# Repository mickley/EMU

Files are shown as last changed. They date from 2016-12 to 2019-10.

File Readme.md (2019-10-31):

# Environmental Microcontroller Units (EMUs)

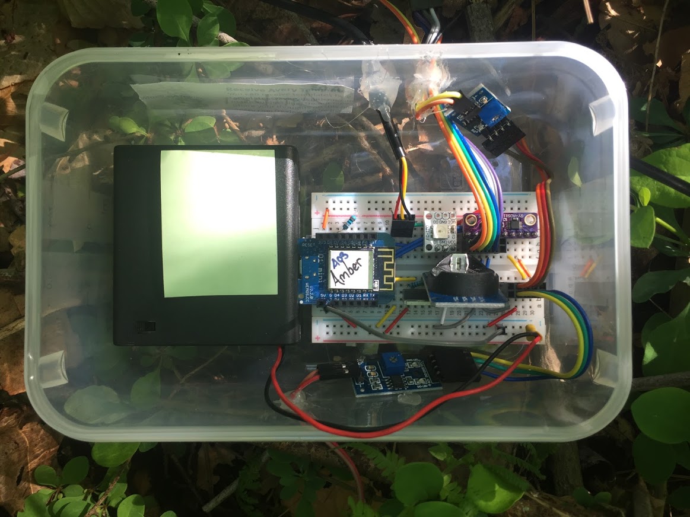
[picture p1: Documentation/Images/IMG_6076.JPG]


This repository stores code, documentation, and analyses for Environmental Microcontroller Units (EMUs). We detail their use in our paper for measuring aspects of microenvironment: temperature, humidity, light, and soil moisture all for less than $20 in hardware costs. However, their flexible nature means that they can be used in a variety of research situations where inexpensive sensors are required.

If this work is useful in your research, please cite our paper:

**Mickley, J. G., T. E. Moore, C. D. Schlichting, A. L. DeRobertis, E. N. Pfisterer, & R. Bagchi (2018). Measuring Microenvironments for Global Change: DIY Environmental Microcontroller Units (EMUs). *Methods in Ecology and Evolution*. 10:578-584. [doi: 10.1111/2041-210X.13128](http://dx.doi.org/10.1111/2041-210X.13128)**

We provide the following:
* [Detailed documentation](/Documentation) including [building EMUs](/Documentation/Building%20EMUs.md), [parts list](/Documentation/), [programming EMUs](/Documentation/EMU%20programming.md), [troubleshooting](/Documentation/Troubleshooting.md), and [circuit diagrams](/Documentation/Diagrams/).
* EMU [operating code](/EMU-Software).
* A [pre-built firmware](/Firmware)
* Our [analyses and data](EMU-Analysis) used in calibrating light and soil moisture sensors and in a field test of EMUs.

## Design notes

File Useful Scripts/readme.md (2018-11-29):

## Useful Scripts

The following scripts are are broadly useful and worth including.  Alternatively, they can be saved as snippets in Esplorer

* **[Tester Scripts](Testers/)** - A collection of scripts to test individual sensors and entire EMUS before deploying.
* **[EMU Module Compiler](module-compiler.lua)** - A script to compile the five lua modules on an EMU.
* **[Ram Test](ram-test.lua)** - A script that can be used to test how much RAM a lua module uses.
* **[Info](info.lua)** - This prints out lots of useful information on the particular Node it's running on.  Includes NodeMCU version, chip, wifi, and filesystem information.
* **[i2c Scanner](i2c_scanner.lua)** - This is a useful scanner that finds out which pins I2C devices are connected to, and what their addresses are.
* **[Lua Tutorial](lua%20tutorial.lua)** - A short tutorial on programming in Lua on NodeMCU firmware.

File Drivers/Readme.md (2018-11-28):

# Drivers

We provide the Windows and Mac drivers for the CH340G chipset used for the Lolin D1 Mini (and many Arduino clones). These drivers are required for a computer to recognise and communicate with an EMU.

See [Computer Setup](/Documentation/Computer%20setup.md) for more information

* [Windows Driver](CH340G%20-%20Windows%20-%20v3.4.2014.8.zip)
* [Mac Driver](CH340G%20-%20Mac.zip)

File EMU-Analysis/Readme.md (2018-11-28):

# Analyses

The following are analyses on EMU performance in the field associated with our paper.

## List of Analyses
* **[Calibration](Analyses/Calibration/Calibration.md)** - Calibration of soil moisture and light sensors.
* **[Sensor Comparisons](Analyses/Fenton%20Hypotheses/Sensor-Comparison.md)** - Comparisons of EMU temperature and humidity readings with those from iButtons and Hobos.
* **[Hypotheses](Analyses/Fenton%20Hypotheses/Fenton_Hypotheses.md)** - A qualitative analysis of how our microenvironmental data matched *a priori* hypotheses for differences between and within transects.
* **[Transect Comparison Models](Analyses/Fenton%20Hypotheses/Transect_Comparison_Models.md)** - A quantitative analysis of the microenvironmental differences between the woods and meadow transects.
* **[Within-Transect Models](Analyses/Fenton%20Hypotheses/Within-Transect_Models.md)** - A quantitative analysis of the microenvironmental differences within transects.
* **[Paired T-Tests](Analyses/Fenton%20Hypotheses/Paired-T-tests.md)** - An alternative analysis of between-transect differences

# Datasets

The following is a list of datasets we collected and use in our analyses.

## List of Datasets
* **[Fenton_soil_calibration.csv](Data/Fenton-soil/Fenton_soil_calibration.csv)** - Data used for soil moisture sensor calibration (from weighing soil every 5 minutes to measure water content).
* **[licor-calibration.csv](Data/licor-calibration/licor-calibration.csv)** - Data used for light sensor calibration (from comparing with LiCor LI-190)
* **[Field Data](Data/EMU-6-21)** - Data collected from EMUs, 
  * [fentondata-all.csv](Data/EMU-6-21/fentondata-all.csv) - Data from all sensor types and transects combined
  * [ibuttons-combined.csv](Data/EMU-6-21/ibuttons-combined.csv) - Data from the two iButtons
  * Data files prefixed with FM are Hobo Pendant data from the meadow transect
  * Data files prefixed with FW are Hobo Pendant data from the woods transect
  * Data files prefixed by a name are EMU data

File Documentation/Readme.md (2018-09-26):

# EMU Documentation

Here, we provide considerable documentation for those wishing to build and use EMUs themselves:

* [A parts list](Parts%20list.md) - including costs and links to online sources
* [Building EMUs](Building%20EMUs.md) - instructions for wiring, soldering, & waterproofing
* [Fritzing & circuit diagrams](Diagrams/) - for those who prefer them
* [Setting up your computer](Computer%20setup.md) - drivers and software setup
* [Programming EMUs](EMU%20programming.md) - flashing the firmware and uploading code
* [Troubleshooting](Troubleshooting.md) - potential problems and their solutions
* [Downloading data from EMUs](Downloading%20data.md) - essential once you have collected data
* [Resources for Learning Lua](Lua%20resources.md) - for those who would like to modify the code

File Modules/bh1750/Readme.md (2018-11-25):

# BH1750FVI Module

The BH1750FVI is a digital 16-bit ambient light sensor with a dynamic range up to 121,556 lux, and a sensitivity as fine as 0.11 lux.

The BH1750FVI has a spectral response of 400–720 nm with peak sensitivity between 470–650 nm, that provides a good approximation of the range of PFD sensors for measuring PAR.

It uses the I²C protocol [BH1750FVI Datasheet](https://www.mouser.com/ds/2/348/bh1750fvi-e-186247.pdf)

### Features
* Maximum range of 121,556 lux
* Maximum sensitivity of 0.11 lux
* Minimum measurement time of 11 ms
* Adjustable range, sensitivity, and measurement time
* Continuous or single measurements

### Required Firmware Modules
* i2c, tmr

### LCD Module Functions

| Function                                                 | Reference                                   |
|----------------------------------------------------------|---------------------------------------------|
| [bh1750.init()](#bh1750init)                             | Initialize the BH1750 sensor                |
| [bh1750.getLux()](#bh1750getlux)                         | Get a light measurement from the sensor     |
| [bh1750.setMode()](#bh1750setmode)                       | Set the sampling mode for the sensor        |
| [bh1750.setMeasurementTime()](#bh1750setmeasurementtime) | Set the sensor measurement time/sensitivity |
| [bh1750.on()](#bh1750on)                                 | Turn on the sensor                          |
| [bh1750.off()](#bh1750off)                               | Turn off the sensor                         |
| [bh1750.reset()](#bh1750reset)                           | Reset the stored light measurement          |

## bh1750.init()
Initializes I²C communication with a BH1750 sensor.  Sets which pins and address to use for I²C communication.

Also turns on the sensor, and sets the default settings.

#### Syntax
`bh1750.init(SDA, SCL, [i2c_addr], [sensor_mode])`

#### Parameters
- `SDA` The GPIO pin to use for SDA
- `SCL` The GPIO pin to use for SCL
- (optional) `i2c_addr` The I²C address to use.  Default is 0x23, and must be either 0x23 or 0x5C
- (optional) `sensor_mode` The sensor measurement mode, see table below. Defaults to Continuous_H

| Mode          | Measurement |Resolution | Neasurement Time |
|---------------|-------------|-----------|------------------|
| Continuous_H  | continuous  | 1 lux     | 180 ms           |
| Continuous_H2 | continuous  | 0.5 lux   | 180 ms           |
| Continuous_L  | continuous  | 4 lux     | 24 ms            |
| OneTime_H     | single      | 1 lux     | 180 ms           |
| OneTime_H2    | single      | 0.5 lux   | 180 ms           |
| OneTime_L     | single      | 4 lux     | 24 ms            |

#### Returns
`true` if a bh1750 sensor is found, `false` if no sensor is present on the I²C pins and address specified.

## bh1750.getLux()

Prints text to the LCD.  You can optionally specify a start position to start printing.  Printing otherwise defaults to [0,0] or the next position in the current row.

#### Syntax
`bh1750.getLux([callback_func])`

#### Parameters
- (optional) `callback_func` A callback function to run after the measurement is completed. The amount of time before the callback function runs is dictated by the sensor mode and measurement time settings, and follows the max value from the datasheet for measurement time, scaled by the MT setting (180 ms default).

#### Returns
Three parameters: `lux, validity, raw`, or `nil` if a callback function is specified. `lux` is the value in lux rounded to 2 decimals that is `false` if the sensor cannot be read. `validity` is a true/false value on whether the sensor value can be trusted (not out of range). `raw` is the raw 16-bit value from the sensor (see datasheet).

When a callback function is run, it is passed the same three parameters: `lux, validity, and raw`.

#### Example
```Lua
-- Load the module
bh1750 = require("bh1750")

-- Initialize the module with SDA = 1, SCL = 2, 0x23 I2C address, and OneTime_H mode
bh1750.init(1, 2, 0x23, OneTime_H)

-- Get the lux value, validity, and raw value from the sensor
bh1750.getLux(function(lx, validity, raw)
    print(lx, validity, raw)
end)

-- Release the module to free up memory
bh1750 = nil
package.loaded["bh1750"] = nil
```

## bh1750.setMode()
Sets the measurement mode of the sensor.  There are three measurement modes that can be configured to either measure continuously, or once on request.

#### Syntax
`bh1750.setMode(sensor_mode)`

#### Parameters
- `sensor_mode` The sensor measurement mode, see table below. Defaults to Continuous_H

| Mode          | Measurement |Resolution | Neasurement Time |
|---------------|-------------|-----------|------------------|
| Continuous_H  | continuous  | 1 lux     | 180 ms           |
| Continuous_H2 | continuous  | 0.5 lux   | 180 ms           |
| Continuous_L  | continuous  | 4 lux     | 24 ms            |
| OneTime_H     | single      | 1 lux     | 180 ms           |
| OneTime_H2    | single      | 0.5 lux   | 180 ms           |
| OneTime_L     | single      | 4 lux     | 24 ms            |

#### Returns
`nil`

## bh1750.setMeasurementTime(MT)

The BH1750 has a setting to adjust the sensor measurement time.  This affects the sensitivity of the sensor, allowing fine-tuning of the sensor's tradeoff between resolution and dynamic range.

By adjusting this setting, resolution can be increased to 0.11 lux, range to 121,556 lux, and measurement time can be decreased to ~11 ms

#### Syntax
`bh1750.setMeasurementTime(MT)`

#### Parameters
- `MT` A scaling parameter for the measurement time.  The default in all modes is 69, and the range can be any integer between 31 (shorter measurement time, less sensitive) and 254 (longer time, more sensitive).  See the table below for examples of how these extremes affect resolution and range.  

| Mode           | MT  | Resolution | Range         | Measurement Time | Default |
|----------------|-----|------------|---------------|------------------|---------|
| Continuous_H   | 69  | 0.83 lux   |  54612.50 lux | 180 ms           | Default |
| Continuous_H   | 31  | 1.85 lux   | 121556.85 lux | 81 ms            |         |
| Continuous_H   | 254 | 0.23 lux   |  14835.68 lux | 663 ms           |         |
| Continuous_H2  | 69  | 0.42 lux   |  27306.85 lux | 180 ms           | Default |
| Continuous_H2  | 31  | 0.93 lux   |  60778.43 lux | 81 ms            |         |
| Continuous_H2  | 254 | 0.11 lux   |   7417.84 lux | 663 ms           |         |
| Continuous_L   | 69  | 3.33 lux   |  54610.00 lux | 24 ms            | Default |
| Continuous_L   | 31  | 7.42 lux   | 121551.29 lux | 11 ms            |         |
| Continuous_L   | 254 | 0.91 lux   |  14835.00 lux | 89 ms            |         |

Parameters for additional values of MT can be calculated with the following formulae:
Measurement time: `180 * MT / 69`
Resolution (H): `1 / 1.2 * 69 / MT`
Range (H): `65535 / 1.2 * 69 / MT`

For H2 mode, resolution and range are further divided by 2. For L mode, resolutions are multiplied by 4, measurement time is scaled from 24 ms instead of 180, and the max raw value for calculating range is 65532.

#### Returns
`nil`

## bh1750.on()
Powers on the sensor the sensor, current draw when on is 120-190 µA.

#### Syntax
`bh1750.on()`

#### Parameters
- None

#### Returns
`nil`

## bh1750.off()
Powers down the sensor, current draw when off is less than 1.0 µA. When powered down, the reset command will not work.

#### Syntax
`bh1750.off()`

#### Parameters
- None

#### Returns
`nil`

## bh1750.reset()
Resets the light measurement stored on the sensor to 0.

#### Syntax
`bh1750.reset()`

#### Parameters
- None

#### Returns
`nil`

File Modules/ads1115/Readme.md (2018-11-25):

# ADS1115 Module

The ADS1115 is a precision analog to digital converter (ADC).  It reads the voltage at an analog pin (A0-A3) and converts that voltage into a number.  

### Features
* Up to four single inputs, or compare the difference between up to 2 sets of inputs.  
* A 15 bit range (0-32767), with the 16th bit denoting sign (+ or -)
* A [programmable gain](#ads1115setgain) setting to change sensitivity
* [Sampling rate](#ads1115setrate) up to 860 samples per second 
* A [comparator](ads1115setcomparator) which can set an alert when measurements cross either a high or low threshhold. 

### Required Firmware Modules
* gpio, i2c, tmr

Further information can be found in the [Datasheet](http://www.ti.com/lit/ds/symlink/ads1115.pdf)

This module uses a lot of RAM: 12-14kB.  Always release the module as soon as you're done with it to free up that memory.  See below for example:

```Lua
-- Release the module to free up memory
ads1115 = nil
package.loaded["ads1115"] = nil
```

### ADS1115 Module Functions

| Function                                         | Reference                                    |
|--------------------------------------------------|----------------------------------------------|
| [ads1115.init()](#ads1115init)                   | Initialize ADS1115 module                    |
| [ads1115.readADC()](#ads1115readadc)             | Read a value from one of the channels        |
| [ads1115.mvolts()](#ads1115mvolts)               | Convert a value into millivolts              |
| [ads1115.setAddress()](#ads1115setaddress)       | Set the I²C address to communicate with      |
| [ads1115.setMode()](#ads1115setmode)             | Set the sampling mode (continuous or single) |
| [ads1115.setPGA()](#ads1115setpga)               | Set the voltage range to measure             |
| [ads1115.setRate()](#ads1115setrate)             | Set the sampling rate                        |
| [ads1115.setComparator()](#ads1115setcomparator) | Enable and configure the comparator          |

## ads1115.init()
Initializes I²C communication with an ADS1115 module.  Sets which pins to use for I²C sets up default measurement configuration.

and tries to automatically find the I²C address the sensor is using.

Also sets default 

#### Syntax
`ads1115.init(SDA, SCL, [i2c_address])`

#### Parameters
- `SDA` The GPIO pin to use for SDA
- `SCL` The GPIO pin to use for SCL
- `i2c_address` The I²C address of the sensor.  Valid addresses are below:

| I²C Address    | ADDR pin connection  |
|----------------|----------------------|
| 0x48 (default) | Ground (or floating) |
| 0x49           | VDD (+)              |
| 0x4A           | SDA                  |
| 0x4B           | SCL                  |

#### Returns
`true` if a sensor is found, `false` if no sensor is present on the I²C pins and address specified.

## ads1115.readADC()
Reads the ADC pins configured by `channel` and returns a 15 bit signed number that signifies the voltage.

The channel can be either single-ended (comparing an ADC pin to Ground) or differential (comparing two ADC pins).  ADC pins are those labeled A0, A1, A2, and A3.  

The number returned ranges between -32767 and 32767, with single-ended channels only returning 0-32767.  The number a voltage corresponds with is determined by the voltage range set in [setPGA()](#ads1115setpga).  For example, if the voltage range is set to +/- 4.096, then +3.3 volts on channel 0 will return 3.3 / 4.096 * 32767 = 26399.  Alternatively, if you multiply the [resolution](#ads1115setpga) by the number returned by readADC(), you will get the voltage.  

Because there is only one register on the sensor to store results in, only one channel can be read at a time.  readADC() takes care of reconfiguring the sensor to read another channel, therefore the following code (below) will work if multiple channels are required.

```Lua
-- Read channel 0
val0 = ads1115.readADC(0)

-- Read channel 1
val1 = ads1115.readADC(1)
```

Because the ADS1115 needs some time to finish measuring a sample, readADC() will not return the latest sample value in single-shot mode unless a callback function is specified.  This allows readADC() to wait until conversion is finished before returning a value through the callback function.

#### Syntax
`ads1115.readADC(channel, [function(value)])`

#### Parameters
- `channel` The ADC channel to measure.  See below for channel options.
- (optional) `function(value)` A callback function to run after conversion is finished.  This function gets the ADC value as an argument.  The amount of time before the callback function runs is dictated by the sampling rate, e.g. a sampling rate of 8 samples/second would run after 1/8 second (125 ms).  

| channel | (+) | (-)    | Type         |
|---------|:---:|:------:|--------------|
| 0       | A0  | Ground | Single       |
| 1       | A1  | Ground | Single       |
| 2       | A2  | Ground | Single       |
| 3       | A3  | Ground | Single       |
| 10      | A0  | A1     | Differential |
| 30      | A0  | A3     | Differential |
| 31      | A1  | A3     | Differential |
| 32      | A2  | A3     | Differential |

#### Returns
the value as a 15 bit signed number (-32767 to 32767), `false` if the channel was invalid, or `nil` if a callback function is specified. 

#### Example
```Lua
-- Load the module
ads1115 = require("ads1115")

-- Initialize the module with SDA = 2, SCL = 1
ads1115.init(2, 1)

-- Get a value from channel A0 and make a callback function to print the result
ads1115.readADC(0, function(val)
    print(val)
end)

-- Release the module to free up memory
ads1115 = nil
package.loaded["ads1115"] = nil
```

## ads1115.mvolts()
Converts the value passed to it to millivolts using the resolution of the current PGA setting (see [setPGA()](#ads1115setpga)).

#### Syntax
`ads1115.mvolts(value)`

#### Parameters
- `value` A value between -32767 and 32767 

#### Returns
value converted into millivolts 

#### Example
```Lua
-- Get a value from channel A0
val = ads1115.readADC(0)

-- Convert to millivolts and print
mvolts = ads1115.mvolts(val)
print(mvolts)
```

## ads1115.setMode()
Sets the sampling mode to either continuous or single shot.  

In continuous mode, the sensor repeatedly measures the configured channel, starting a new measurement as soon as the previous is finished and storing the result in the conversion register.

In single shot mode, the sensor measures the configured channel once, and then goes into power down/sleep mode where it uses minimal power.  

#### Syntax
`ads1115.setMode(mode)`

#### Parameters
- `mode` The mode to use: `"single"` for single-shot mode or `"continuous"` for continuous mode.  If anything else is specified, it defaults to continuous

#### Returns
`nil`

#### Example
```Lua
-- Set the sensor to use continuous mode
ads1115.setMode("continuous")
```

## ads1115.setPGA()
The ADS1115 has a built-in programmable gain amplifier (PGA).  This means that the sensitivity can be adjusted to measure smaller ranges of voltages at higher accuracy.  The PGA can be set anywhere from a gain of 2/3 (corresponding to +/- 6.144 volts) to a gain of 16 (corresponding to +/- 256 millivolts).  This allows for a resolution as low as 7.8 microvolts per bit at a gain of 16.  

Note that this is independent of the voltage range that the ADS1115 can actually handle.  That is specified as 0.3 volts more than the voltage the sensor is running on (VDD) or less than Gnd.  **Anything beyond VDD + 0.3 V or GND - 0.3V can damage the sensor**.  

If, for example, the sensor is configured with a gain of 16 and the ADC pin is fed 3.3V, the ADC will simply return the highest value possible (32767)

#### Syntax
`ads1115.setPGA(setrange)`

#### Parameters
- `setrange` The voltage range to set the PGA to.  See below for possible setrange settings:

| setrange        | Gain | Voltage range   | Resolution |
|:---------------:|:----:|:---------------:|:----------:| 
| 6.144 (default) | 2/3  | +/- 6.144 Volts | 0.18750 mV |
| 4.096           | 1    | +/- 4.096 Volts | 0.12500 mV |
| 2.048           | 2    | +/- 2.048 Volts | 0.06250 mV |
| 1.024           | 4    | +/- 1.024 Volts | 0.03125 mV |
| 0.512           | 8    | +/- 0.512 Volts | 0.01563 mV |
| 0.256           | 16   | +/- 0.256 Volts | 0.00781 mV |

#### Returns
`true` if the setrange was valid, `false` if the setrange was invalid

#### Example
```Lua
-- Set the PGA to use +/- 1.024 volts
ads1115.setPGA(1.024)
```

## ads1115.setRate()
This sets the number of samples to acquire per second (in continuous mode), or the length of time to take a sample (in single shot mode).  Slower rates are more precise, but use more power in single shot mode since the ADS1115 spends less time in sleep mode.  See [setMode()](#ads1115setmode) for more on the modes.  

#### Syntax
`ads1115.setRate(sampling_rate)`

#### Parameters
- `sampling_rate` The sampling rate.  See below for the possible rate settings:

| Rate<br/>(samples/second) | Sampling time<br/>(milliseconds) |
|:-------------------------:|:--------------------------------:|
| 8                         | 125                              |
| 16                        | 63                               |
| 32                        | 32                               |
| 64                        | 16                               |
| 128 (default)             | 8                                |
| 250                       | 4                                |
| 475                       | 3                                |
| 860                       | 2                                |

#### Returns
`true` if the rate was valid, `false` if the rate was invalid

#### Example
```Lua
-- Set the sampling rate to 860 samples per second
ads1115.setRate(860)
```

## ads1115.setComparator()
Enables and configures the comparator.  

The ADS1115 has a comparator function, which compares the output of one of the ADC channels to a low and high threshold.  It controls the ALERT pin, which can output a signal when certain conditions are met.  This signal can be programmed to be either HIGH (+) or LOW (-).

Two modes are provided:
* Hysteresis mode will activate when the high threshold is met and deactivate when the low threshold is met
* Window mode will activate when either the high threshold or the low threshold are met.

Both thresholds take the form of a number between -32767 and 32767 that corresponds to a voltage at the given [PGA](#ads1115setpga) setting.  For example, at +/- 6.144 Volts, a 3 volt threshold would correspond to 3 / 6.144 * 32767 = 16000.

Additionally, there is a latch function, that when enabled will keep the ALERT pin activated even after the comparator conditions are no longer met.  When latched, it can only be deactivated by taking another reading via [readADC()](#ads1115readadc) when comparator conditions are within the thresholds. 

#### Syntax
`ads1115.setComparator(mode, [low, high, latch, queue, alert])`

#### Parameters
- `mode` Comparator mode.  Set to `"hysteresis"` for hysteresis mode, `"window"` for window mode, or `"disable"` to disable the comparator.
- (optional) `low` The lower threshold for the comparator.  Must be between -32767 and 32767 and < the high threshold. Default is 0
- (optional) `high` The higher threshold for the comparator.  Must be between -32767 and 32767 and > the low threshold. Default is 32767
- (optional) `latch` Set to `true` to enable a latch or `false` (default) to disable.
- (optional) `queue` Set how many measurements must cross the threshold to trigger activation.  Valid options are `1` (default), `2`, and `4`.
- (optional) `alert` Set to `"high"` or `"low"` (default) to set whether the ALERT pin is activated as HIGH (+) or Low (-) when triggered by the comparator.

#### Returns
`true` if comparator enabled, `false` if comparator disabled and settings invalid

#### Example
```Lua
-- Load the module
ads1115 = require("ads1115")

-- Initialize the module with SDA = 2, SCL = 1
ads1115.init(2, 1)

-- Set the sensor to measure continuously
ads1115.setMode("continuous")

-- Trigger when voltage goes above 3V (3 / 6.144 * 32767 = 15999)
-- Turn off trigger when voltage goes below 2V (2 / 6.144 * 32767 = 10666)
-- Only require one measurement to cross threshold to trigger
-- Alert pin will go low when activated
-- No latching, hysteresis mode
ads1115.setComparator("hysteresis", 10667, 16000)

-- Get a value from channel A0 and print
val = ads1115.readADC(0)
print(val)

-- Release the module to free up the memory
ads1115 = nil
package.loaded["ads1115"] = nil
```

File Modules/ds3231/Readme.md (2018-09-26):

# DS3231/DS3232 Real Time Clock (RTC) Module

The [DS3231](https://www.maximintegrated.com/en/products/digital/real-time-clocks/DS3231.html) is an extremely accurate battery-backed Real Time Clock (RTC).  It provides a way to accurately get the current time, and provides alarms to schedule actions at specific times.  

While the module is built for the DS3231, it should also work on the [DS3232](https://www.maximintegrated.com/en/products/digital/real-time-clocks/DS3232.html).  See this [comparison of Maxim Real Time Clocks](https://www.maximintegrated.com/en/app-notes/index.mvp/id/5143) for more information.

### Features
* Two alarms that when triggered can send either a LOW output or a square wave over the alarm pin (INT/SQW)
* A 32khz square wave output on the 32kHz pin
* Battery-backed timekeeping using a CR2032 battery that lasts years, and can run the alarm outputs and square waves
* An 8-bit temperature sensor with 0.25 °C resolution and 3 °C accuracy
* This module can return the date and time in a variety of formats

### Required Firmware Modules
* i2c, rtctime

Further information on the DS3231 can be found in the [Datasheet](https://datasheets.maximintegrated.com/en/ds/DS3231.pdf)

**Note:** This module uses a lot of RAM: 12-15kB.  Always release the module as soon as you're done with it to free up that memory.  See below for example:

```Lua
-- Release the module to free up memory
ds3231 = nil
package.loaded["ds3231"] = nil
```

### DS3231 Module Functions

| Function                                             | Reference                                                |
|------------------------------------------------------|----------------------------------------------------------|
| [ds3231.init()](#ds3231init)                         | Initialize the DS3231 module                             |
| [ds3231.config()](#ds3231config)                     | Configure options, mostly for the outputs                |
| [ds3231.setTime()](#ds3231settime)                   | Set the current time                                     |
| [ds3231.getTime()](#ds3231gettime)                   | Get the current time                                     |
| [ds3231.setAlarm()](#ds3231setalarm)                 | Set one of the two alarms                                |
| [ds3231.changeAlarmState()](#ds3231changealarmstate) | Enable or disable an alarm                               |
| [ds3231.rearmAlarms()](#ds3231rearmalarms)           | Re-arm both alarms                                       |
| [ds3231.format()](#ds3231format)                     | Convert a numeric time into a formatted timestamp string |
| [ds3231.getTemp()](#ds3231gettemp)                   | Gets the current temperature                             |

## ds3231.init()

Initializes I²C communication with the RTC module. Sets which pins and address to use for I²C communication.

Also optionally sets the timezone offset to use for time formatting.  

#### Syntax
`ds3231.init(sda, scl, [i2c_address], [timezone])`

#### Parameters
- `sda` The GPIO pin to use for SDA
- `scl` The GPIO pin to use for SCL
- (optional) `i2c_address` The I²C address to use. Default is 0x68, and must be between 0x68 and 0x6F
- (optional) `timezone` The timezone offset to use.  Default is -5 (EST)

#### Returns
`true` if a RTC is found, `false` if no RTC is present on the I²C pins and address specified.

## ds3231.config()

Configures various settings on the DS3231 dealing with what to run while only on battery power, how to handle alarms, and set up outputs on the two output pins: INT/SQW and 32kHz.  

#### Syntax
`ds3231.config([mode], [SQRate], [BBSQW], [disableOnBatt], [disable32kHz], [BB32kHz], [TCRate])`

#### Parameters
- (optional) `mode` The alarm output mode for the INT/SQW pin.  `"INT"` will make the pin LOW if an alarm triggers.  `"SQW"` will output a square wave with the frequency set in `SQRate`.  The default is `"INT"`
- (optional) `SQRate` The frequency of the square wave for alarm-triggered square wave output.  See SQRate table below.  The default is `1`
- (optional) `BBSQW` Enables square wave output while only powered by the battery.  This applies only to the INT/SQW pin.  `true` to enable, `false` to disable.  The default is `false`
- (optional) `disableOnBatt` Disables the clock while only powered by the battery. `true` to disable, `false` to enable.  The default is `false`.  If the clock is disabled, it will stop keeping time when the main power is removed, even if a battery is present.
- (optional) `disable32kHz` Disables the constant 32.768 kHz output on the 32kHz pin. `true` to disable, `false` to enable.  The default is `false`
- (optional) `BB32kHz` **Not yet implemented** On the DS3232 this enables the 32kHz functionality while powered only by the battery.  For the DS3231, the 32kHz output works regardless of power supply when enabled.  
- (optional) `TCRate` **Not yet implemented** On the DS3232, allows changing of the interval between temperature conversions.  On the DS3231, the interval is fixed at 64 seconds.  

| SQRate | Frequency        |
---------|------------------|
| 1      | 1 Hz output      |
| 1024   | 1.024 kHz output |
| 4096   | 4.096 kHz output |
| 8192   | 8.19 2kHz output |

#### Returns
`nil`

#### Example
```Lua
-- Set alarms to trigger a LOW interrupt on the INT/SQW pin instead of a square wave
-- Disable square wave output but enable timekeeping while only on battery power
-- Disable the 32kHz output
ds3231.config("INT", nil, false, false, true)
```

## ds3231.setTime()

Sets the current date and time on the DS3231 based on the date/time parameters given.  If a 2032 battery is not installed, then the time will be lost as soon as the DS3231 loses power.  However, if a battery is installed, the DS3231 will continue keeping time from this set point.  

Ideally, set up the command for 30 seconds ahead of time and run it right as the seconds of your reference clock reachs your set point to sync to your reference clock.

#### Syntax
`ds3231.setTime(second, minute, hour, day, date, month, year)`

#### Parameters
- `second` The current seconds (0-59)
- `minute` The current minutes (0-59)
- `hour` The current hour in 24-hour time (0-23)
- `day` The current day of the week (1-7), with 1 = Sunday and 7 = Saturday
- `date` The current day of the month (1-31)
- `month` The current month (1-12)
- `year` The current year in either 2-digit or 4-digit format.

#### Returns
`nil`

#### Example
```Lua
-- Set the current date and time to Wednesday Feb 22nd 2017 16:45:15 (Wednesday = day 4 of the week)
ds3231.setTime(15, 45, 16, 4, 22, 2, 2017)
```

## ds3231.getTime()

Gets the current date and time and returns either raw numbers for seconds, minutes, hours, day of week, day of month, month, and year, or a formatted string using a modified subset of [POSIX/strftime formatting codes](https://www.gnu.org/software/libc/manual/html_node/Formatting-Calendar-Time.html).

Optionally, it can also sync the current time from the DS3231 to the [rtctime](https://nodemcu.readthedocs.io/en/master/en/modules/rtctime/) firmware module in a similar way to [sntp.sync()](https://nodemcu.readthedocs.io/en/master/en/modules/sntp/#sntpsync).  For this to work, the rtctime module is required, however if no syncing takes place, it can be left off the firmware.

#### Syntax
`ds3231.getTime([format], [sync])`

#### Parameters
- (optional) `format` The format to return the date/time in.  The default is `"raw"`.  See the format table below. With the exception of `"raw"` formats can be strung together in a string along with other characters, e.g. `"Current Time: %H:%M:%S"`.
- (optional) `sync` Sync the time with the firmware rtctime module `true` or don't sync `false`.  The default is `false`.

| format | Description                                                                                     |
---------|-------------------------------------------------------------------------------------------------|
| raw    | Returns the raw values (7 numbers starting with seconds) instead of a formatted string.         |
| %D     | Returns the date in mm/dd/yy format.  Equivalent to %m/%d/%y                                    |
| %r     | Returns the time in 12-hour AM/PM format.  Equivalent to %i:%M:%S %p                            |
| %T     | Returns the time in 24-hour format.  Equivalent to %H:%M:%S                                     |
| %f     | Returns the ISO-8601 standard format YYYY-mm-ddTHH:MM:SS+tz. Equivalent to %Y-%m-%dT%H:%M:%S%z  |
| %R     | Returns the time in R's POSIXct format: YYYY-mm-dd HH:MM:SS. Equivalent to %Y-%m-%d %H:%M:%S    |
| %a     | Abbreviated day of week (3 letters)                                                             |
| %A     | Full day of week                                                                                |
| %b     | Abbreviated month name                                                                          |
| %B     | Full month name                                                                                 |
| %c     | Day of the month without leading zeros                                                          |
| %d     | Day of the month with leading zeros                                                             |
| %h     | 24-hour hours without leading zeros                                                             |
| %H     | 24-hour hours with leading zeros                                                                |
| %i     | 12-hour hours without leading zeros                                                             |
| %I     | 12-hour hours with leading zeros                                                                |
| %m     | Month with leading zeros                                                                        |
| %M     | Minutes with leading zeros                                                                      |
| %n     | Month without leading zeros                                                                     |
| %p     | AM/PM indicator (for use with 12-hour time)                                                     |
| %s     | Unix Timestamp: number of seconds since the Unix epoch: 1/1/1970 00:00:00                       |
| %S     | Seconds with leading zeros                                                                      |
| %w     | Day of week as a number (0-6) with Sunday = 0                                                   |
| %y     | 2-digit year                                                                                    |
| %Y     | 4-digit year                                                                                    |
| %z     | Timezone offset                                                                                 |
| %%     | The `%` character                                                                               |

#### Returns
`seconds, minutes, hours, day, date, month, year` if format is `"raw"` or `nil`.  Or a formatted string according to the format argument.

#### Example
```Lua
-- Load the module
ds3231 = require("ds3231")

-- Initialize the module with SDA = 1, SCL = 2
ds3231.init(1, 2)

-- Get the raw numbers for all of the date/time parameters
seconds, minutes, hours, day, date, month, year = ds3231.getTime("raw")

-- Print out the raw numbers
print(seconds, minutes, hours, day, date, month, year)

-- Only get the hours, not saving the other values
_, _, hours = ds3231.getTime("raw")

-- Print out the hours
print(hours)

-- Get a formatted time string, also syncing the current time to the rtctime module
timestring = ds3231.getTime("%D %T", true);

-- Print the formatted time string
print(timestring)

-- Don't forget to release it after use
ds3231 = nil
package.loaded["ds3231"]=nil
```

## ds3231.setAlarm()

This sets one of the two alarms on the DS3231.  Alarm #1 supports seconds precision and Alarm #2 only supports minutes precision.  

When either of the alarms trigger, they either set the INT/SQW pin LOW (INT mode) or output a square wave of 1 Hz to 8.192 kHz (SQW mode).  This behavior can be configured using [ds3231.config()](#ds3231config).  

Regardless of which trigger they use, the trigger continues to be active until [ds3231.setAlarm()](#ds3231setalarm) is called again or both alarms are re-armed using [ds3231.rearmAlarms()](#ds3231rearmalarms).

#### Syntax
`ds3231.setAlarm(alarm, alarmType, [second], [minute], [hour], [daydate])`

#### Parameters
- `alarm` The alarm to set: `1` or `2`
- `alarmType` The type/frequency of alarm to set.  See the alarmType table below.  
- (optional) `seconds` The seconds to trigger at (0-59).  Required for all alarmTypes but `ds3231.EVERYSECOND` or `ds3231.EVERYMINUTE`.  Ignored for alarm #2.  
- (optional) `minutes` The minutes to trigger at (0-59).  Required for all alarmTypes but `ds3231.EVERYSECOND`, `ds3231.EVERYMINUTE`, and `ds3231.SECOND`
- (optional) `hours` The hours to trigger at (0-23).  Required for the alarmTypes `ds3231.HOUR`, `ds3231.DAY`, `ds3231.DATE`
- (optional) `weekday/date` For the `ds3231.DAY` alarmType, this is the day of the week (1 = Sunday, 7 = Saturday).  For the `ds3231.DATE` alarmType, this is the day of the month (1-31). Only required for alarmTypes `ds3231.DAY` and `ds3231.DATE`

| alarmType          | Description                                                                                |
|--------------------|--------------------------------------------------------------------------------------------|
| ds3231.EVERYSECOND | Only works with alarm 1 and triggers every second                                          |
| ds3231.EVERYMINUTE | Only works with alarm 2 and triggers every minute (00 seconds)                             |
| ds3231.SECOND      | Triggers when time matches the seconds parameter                                           |
| ds3231.MINUTE      | Triggers when time matches the seconds and minutes parameters                              |
| ds3231.HOUR        | Triggers when time matches the seconds, minutes, and hours parameters                      |
| ds3231.DAY         | Triggers when time matches the seconds, minutes, hours, and weekday parameters             |
| ds3231.DATE        | Triggers when time matches the seconds, minutes, hours, and date (day of month) parameters |

#### Returns
`nil`

#### Example
```Lua
-- Set alarm 1 to trigger hourly at 30 minutes past the hour
ds3231.setAlarm(1, ds3231.MINUTE, 0, 30)

-- Set alarm 2 to trigger on Mondays at 8 AM
ds3231.setAlarm(2, ds3231.DAY, 0, 0, 8, 2)
```

## ds3231.changeAlarmState()

This enables or disables an alarm.  It will not reset an alarm that has already triggered.  

#### Syntax
`ds3231.changeAlarmState(alarm, enable)`

#### Parameters
- `alarm` The alarm to enable or disable: `1` or `2`
- `enable` Enable the alarm if `true`, disable if  `false`

#### Returns
`nil`

#### Example
```Lua
-- Disable alarm #1
ds3231.changeAlarmState(1, false)

-- Enable alarm #2
ds3231.changeAlarmState(2, true)
```

## ds3231.rearmAlarms()

This resets both alarms, turning off the alarm output if they have triggered.  The alarms need to remain enabled to re-trigger.

#### Syntax
`ds3231.rearmAlarms()`

#### Returns
`nil`

## ds3231.format()

Takes raw date/time values and formats them, returning a formatted date/time string.  

#### Syntax
`ds3231.format(format, second, minute, hour, dayofweek, date, month, year, [timezone], [sync])`

#### Parameters
- `format` The format to use.  Uses the same POSIX/strftime formats detailed in [ds3231.getTime()](#ds3231gettime)
- `second` The number of seconds (0-59)
- `minute` The number of minutes (0-59)
- `hour` The number of hours (0-23)
- `dayofweek` The day of the week (1 = Sunday, 7 = Saturday)
- `date` The day of the month (1-31
- `month` The month (1-12)
- `year` The year in 4-digit format
- (optional) `timezone` The timezone offset. The default is `0`
- (optional) `sync` Sync the time with the firmware rtctime module `true` or don't sync `false`.  The default is `false`.

#### Returns
`nil`

#### Example
```Lua
-- Only get the minutes, not saving the other values
seconds, minutes, hours = ds3231.getTime("raw")

-- Add 15 to the minutes
minutes = minutes + 15

-- Get the formatted time 15 minutes from now.  Doesn't matter what the last 4 values are
timestring = format("%T", seconds, minutes, hours, 1, 1, 1, 2017)
```

## ds3231.getTemp()

The DS3231 has a temperature sensor that it uses to temperature-correct its timekeeping.  This temperature sensor has ±3°C accuracy and 0.25 °C resolution, and can be be read.  

The latest temperature value is updated every 64 seconds.  On the DS3232, this is configurable from 64-512 seconds, conserving some of power with less frequent updates.  

#### Syntax
`ds3231.getTemp()`

#### Returns
The latest temperature reading in °C

#### Example
```Lua
-- Get the temperature
temp = ds3231.getTemp()

-- Print out the temperature
print(temp)
```

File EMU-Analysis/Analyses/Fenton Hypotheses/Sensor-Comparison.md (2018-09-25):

---
title: "Comparison Among Sensor Types"
author: "James Mickley"
output:
  html_document:
    keep_md: yes
    theme: readable
  html_notebook:
    theme: readable
graphics: yes
editor_options: 
  chunk_output_type: console
---

### Overview

This analysis compares the results for the EMU, Hobo Pendant, and iButton at the first site in each of the two transects.  

### Temperature

Differences in temperature between EMUs relative to Hobo Pendants at all positions in the transects.

Hobos tend to read high, especially during the day.  Strongly suggests heat trapped from sun.

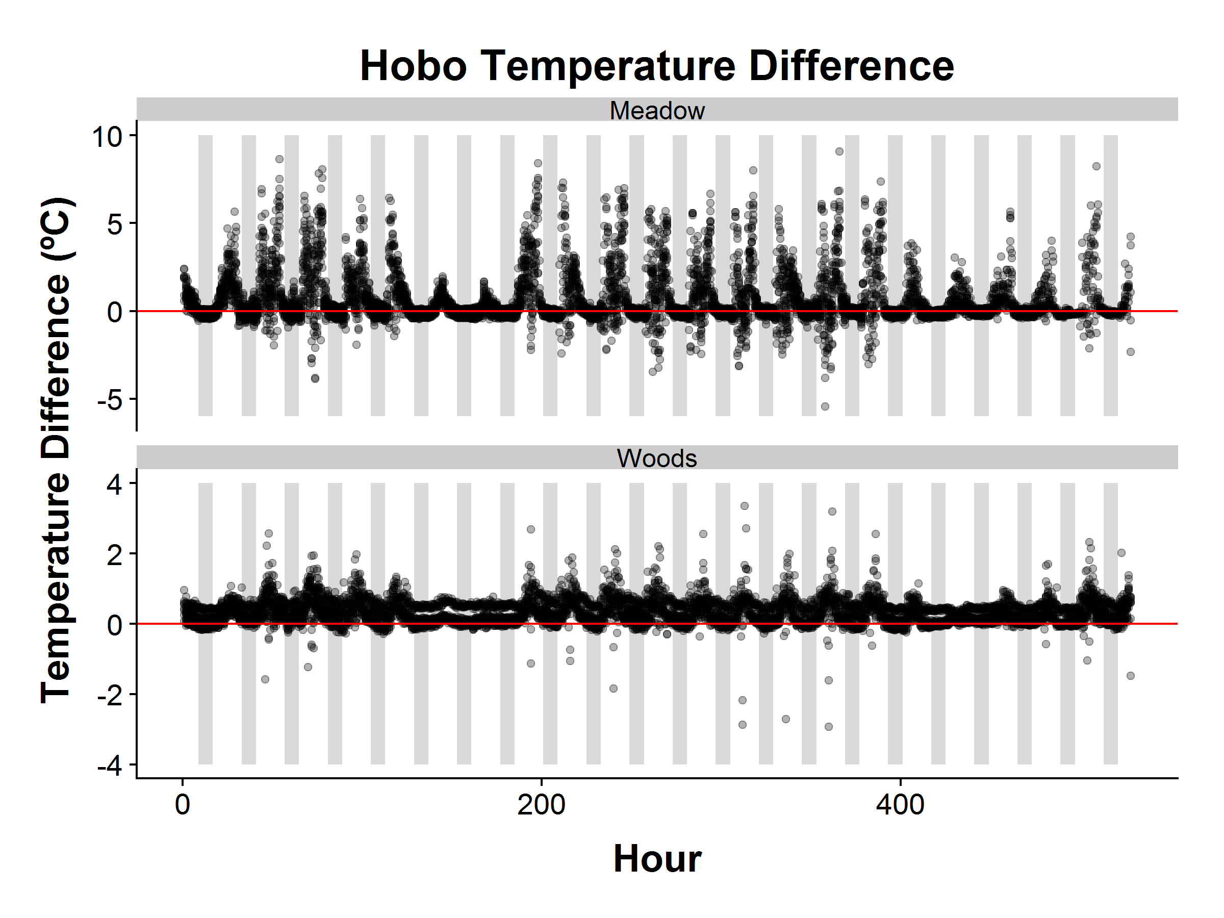
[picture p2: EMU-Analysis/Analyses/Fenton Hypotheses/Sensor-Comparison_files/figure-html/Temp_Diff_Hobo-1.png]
<!-- -->

Differences in temperature between EMUs relative to iButtons at the first position of each transect.

Prior to hour 98, the iButtons had fallen on the ground, so you are seeing the difference between ground temperature and that of 10 cm above.

There is minimal difference in temperature between the iButtons and Hobos on both transects from hour 98 to 190.  After 190, the meadow BME280 started failing. Subsequent values may be inaccurate.

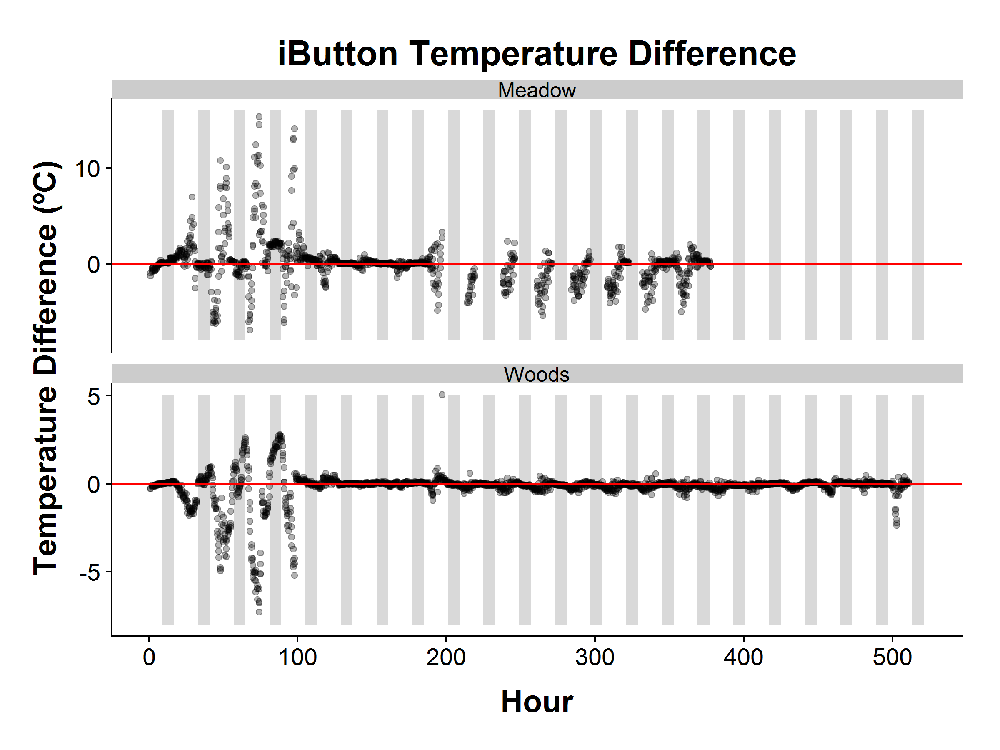
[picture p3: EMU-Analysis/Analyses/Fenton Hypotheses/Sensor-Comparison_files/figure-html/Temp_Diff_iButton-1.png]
<!-- -->

### Humidity

Differences in humidity between EMUs relative to iButtons at the first position of each transect.

Prior to hour 98, the iButtons had fallen on the ground, so this is the difference between ground temperature and that of 10 cm above.

It looks like humidity is lower during the day with the iButton on the meadow transect, and generally higher at all times in the woods.

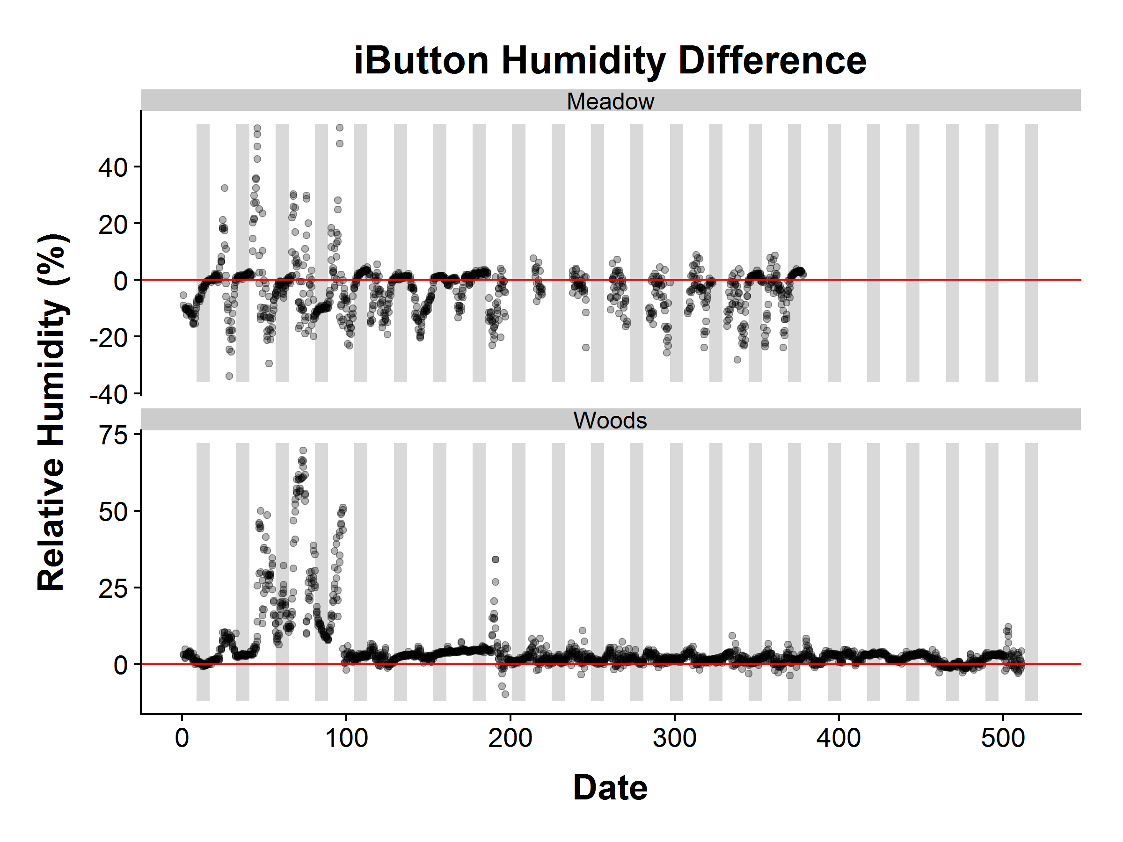
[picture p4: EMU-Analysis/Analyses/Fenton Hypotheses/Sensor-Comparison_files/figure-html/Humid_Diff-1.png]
<!-- -->

## Comparisons between EMU & iButton/Hobo Pendant for Woods transect

The Hobo Pendant reads slightly high on temperature (by about 2ºC).  Presumably it's getting heated inside of its enclosed case.

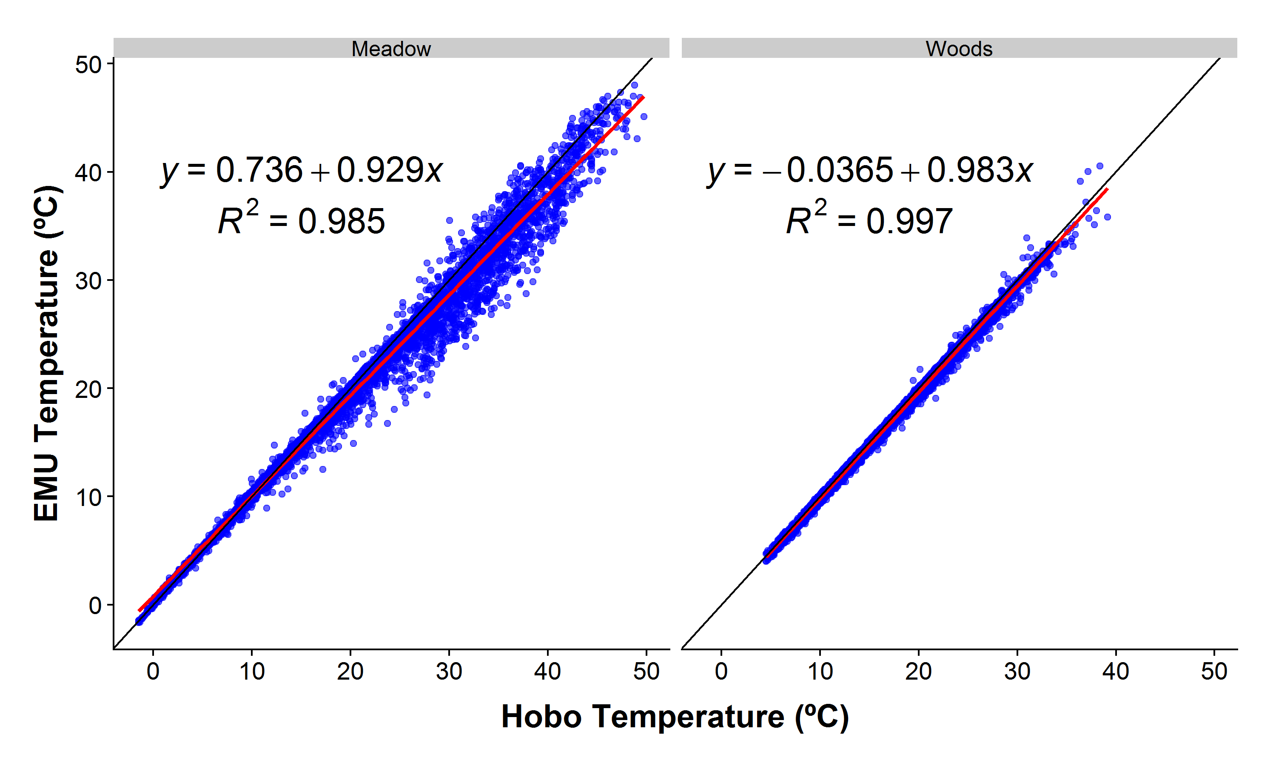
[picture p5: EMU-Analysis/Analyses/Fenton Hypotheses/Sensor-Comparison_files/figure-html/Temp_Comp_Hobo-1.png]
<!-- -->

The iButtons read slightly lower than the EMU when it's cold, and slightly higher when hot.  Presumably, this is in response to the metal enclosure.

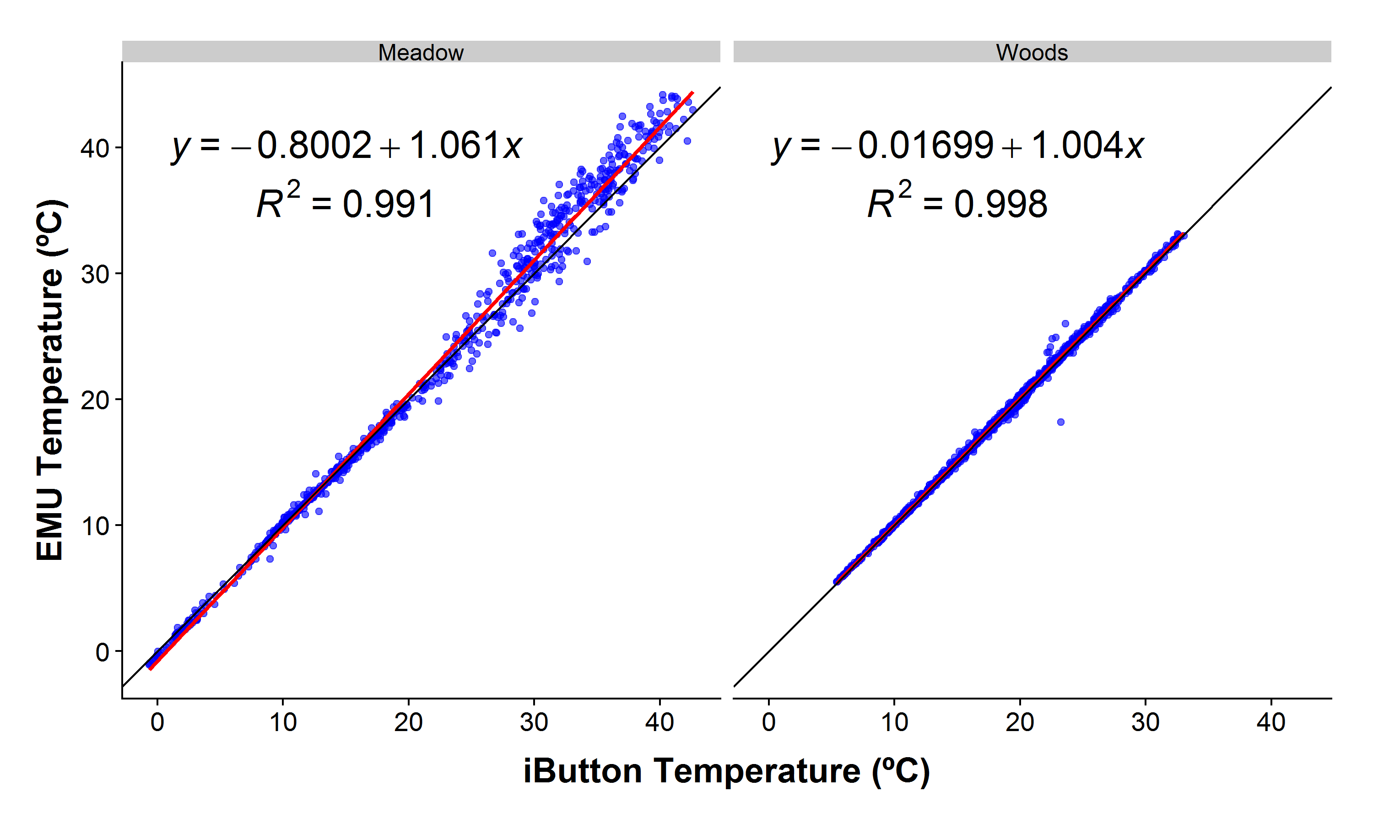
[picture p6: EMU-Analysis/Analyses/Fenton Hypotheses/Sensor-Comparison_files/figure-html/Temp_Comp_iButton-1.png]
<!-- -->

Comparing iButtons to Hobos, we see that hobos read too high for anything over about 10C.  Again evidence of self-heating.

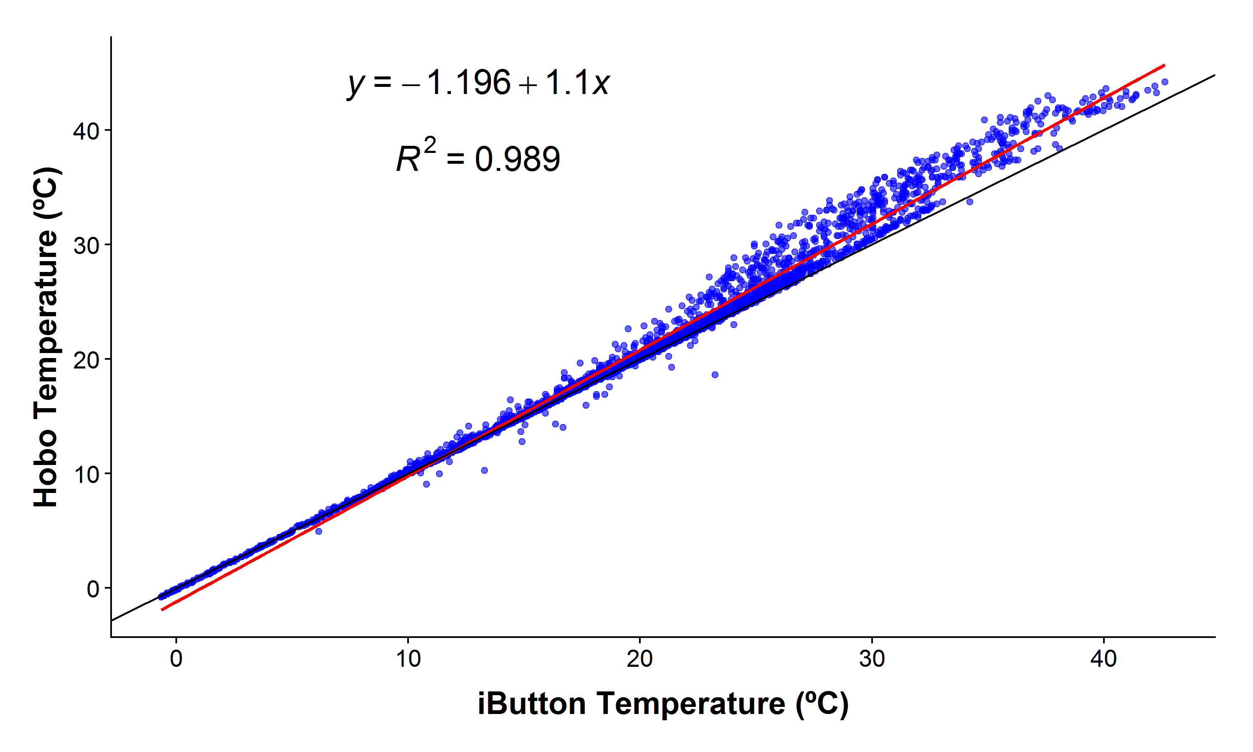
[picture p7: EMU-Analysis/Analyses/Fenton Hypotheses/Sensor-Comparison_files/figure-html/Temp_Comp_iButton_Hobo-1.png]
<!-- -->

### Humidity

The iButtons have slightly higher humidity (3-5% or so) in the Woods.  They also can return values higher than 100%.  

In the meadow, the BME280 failed, and I think all the humidity values are bogus.

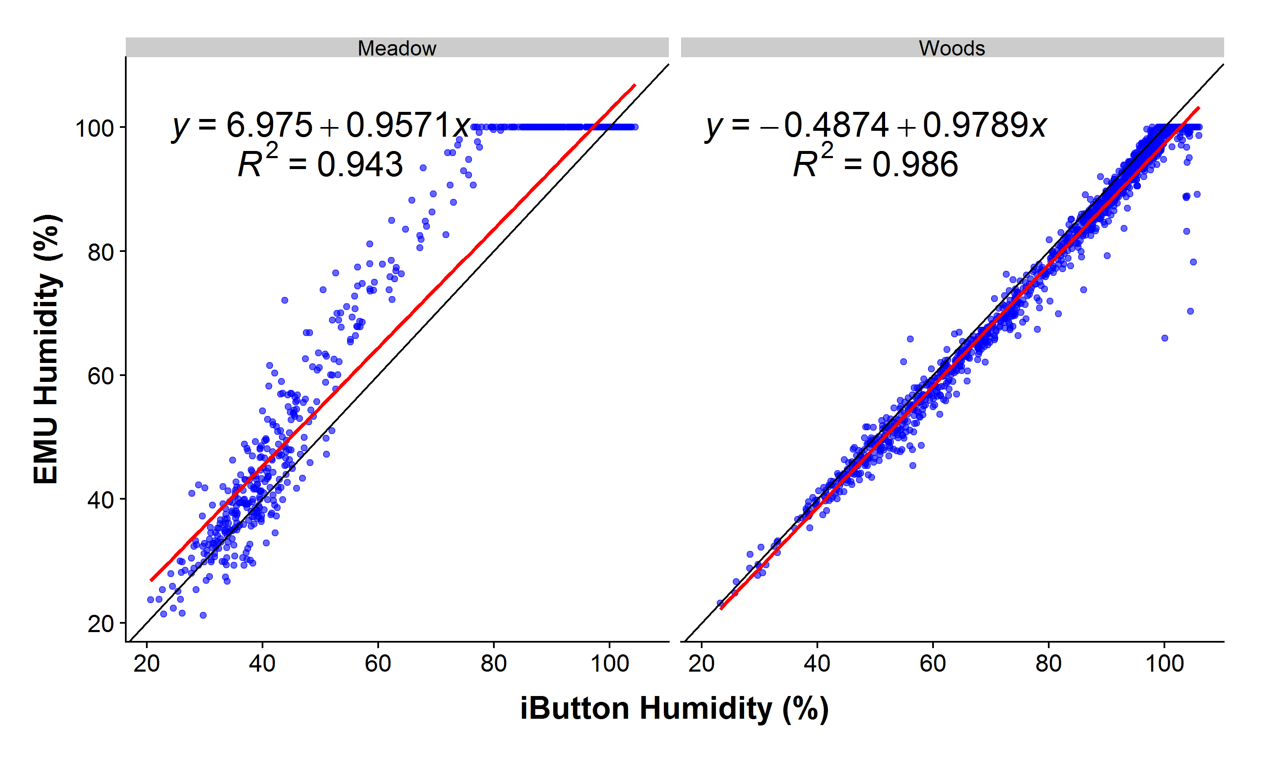
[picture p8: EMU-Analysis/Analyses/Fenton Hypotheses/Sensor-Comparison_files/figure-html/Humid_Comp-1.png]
<!-- -->

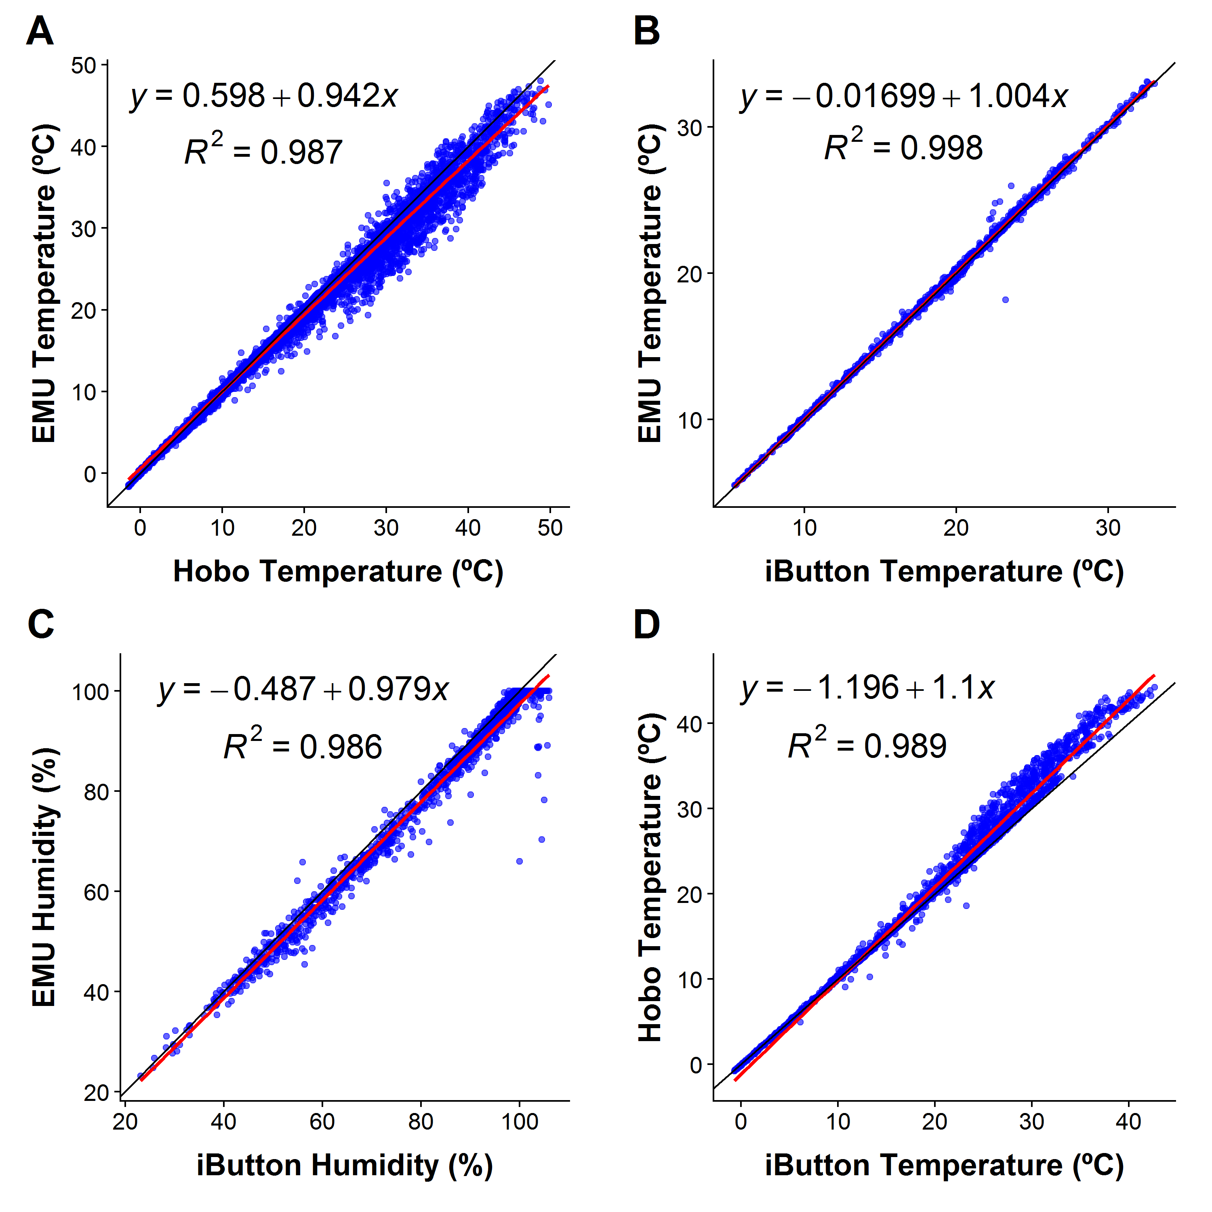
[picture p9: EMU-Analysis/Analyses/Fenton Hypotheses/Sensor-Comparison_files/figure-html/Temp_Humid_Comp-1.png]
<!-- -->

### Session Information

```
R version 3.4.3 (2017-11-30)
Platform: x86_64-w64-mingw32/x64 (64-bit)
Running under: Windows 7 x64 (build 7601) Service Pack 1

Matrix products: default

locale:
[1] LC_COLLATE=English_United States.1252 
[2] LC_CTYPE=English_United States.1252   
[3] LC_MONETARY=English_United States.1252
[4] LC_NUMERIC=C                          
[5] LC_TIME=English_United States.1252    

attached base packages:
[1] stats     graphics  grDevices utils     datasets  methods   base     

other attached packages:
 [1] bindrcpp_0.2.2  maptools_0.9-4  sp_1.3-1        rgeos_0.3-28   
 [5] lubridate_1.7.4 ggpmisc_0.3.0   cowplot_0.9.3   forcats_0.3.0  
 [9] stringr_1.3.0   dplyr_0.7.6     purrr_0.2.4     readr_1.1.1    
[13] tidyr_0.8.0     tibble_1.4.2    ggplot2_3.0.0   tidyverse_1.2.1

loaded via a namespace (and not attached):
 [1] tidyselect_0.2.4 reshape2_1.4.3   haven_1.1.1      lattice_0.20-35 
 [5] colorspace_1.3-2 htmltools_0.3.6  yaml_2.1.18      rlang_0.2.2     
 [9] pillar_1.2.2     foreign_0.8-69   glue_1.2.0       withr_2.1.2     
[13] modelr_0.1.1     readxl_1.1.0     bindr_0.1.1      plyr_1.8.4      
[17] munsell_0.4.3    gtable_0.2.0     cellranger_1.1.0 rvest_0.3.2     
[21] codetools_0.2-15 psych_1.8.4      evaluate_0.10.1  labeling_0.3    
[25] knitr_1.20       parallel_3.4.3   broom_0.4.4      Rcpp_0.12.16    
[29] polynom_1.3-9    scales_0.5.0     backports_1.1.2  jsonlite_1.5    
[33] mnormt_1.5-5     hms_0.4.2        digest_0.6.15    stringi_1.1.7   
[37] grid_3.4.3       rprojroot_1.3-2  cli_1.0.0        tools_3.4.3     
[41] magrittr_1.5     lazyeval_0.2.1   crayon_1.3.4     pkgconfig_2.0.1 
[45] xml2_1.2.0       assertthat_0.2.0 rmarkdown_1.9    httr_1.3.1      
[49] rstudioapi_0.7   R6_2.2.2         nlme_3.1-131     compiler_3.4.3  
```

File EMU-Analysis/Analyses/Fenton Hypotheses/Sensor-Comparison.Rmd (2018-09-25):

---
title: "Comparison Among Sensor Types"
author: "James Mickley"
output:
  html_document:
    keep_md: yes
    theme: readable
  html_notebook:
    theme: readable
graphics: yes
editor_options: 
  chunk_output_type: console
---

```{r setup, include = F}
# @@@@@@@@@@@@@@@@@@@@@@@@@@@@@@@@@@@@@@@@@@@@@@@@@@
# @@@@@ Knitr Options
# @@@@@@@@@@@@@@@@@@@@@@@@@@@@@@@@@@@@@@@@@@@@@@@@@@

# Set root directory to the project directory
knitr::opts_knit$set(root.dir = rprojroot::find_rstudio_root_file())

# Set default knitr options: 
# Suppress warnings and messages, cache chunks, 
#  set default figure size to 6x8 at 300 dpi, and save a png and pdf
knitr::opts_chunk$set(warning = F, message = F, collapse = T, cache = T,
    fig.height = 6, fig.width = 8, dpi = 300, # 6x8" @ 300dpi:1800x2400=4.3MP
    dev = c('png', 'pdf'), dev.args = list(pdf = list(onefile = F)))

```

### Overview

This analysis compares the results for the EMU, Hobo Pendant, and iButton at the first site in each of the two transects.  

```{r 'Main_Code', include = F, cache = F}

# @@@@@@@@@@@@@@@@@@@@@@@@@@@@@@@@@@@@@@@@@@@@@@@@@@
# @@@@@ Setup - This code is run, but output is hidden
# @@@@@@@@@@@@@@@@@@@@@@@@@@@@@@@@@@@@@@@@@@@@@@@@@@

# Load Packages
require(tidyverse) # Needed for data wrangling
require(cowplot) # Needed for publication-quality ggplots
require(ggpmisc) # Needed for lm equations on graphs
require(lubridate) # Needed for date wrangling
require(rgeos) # Required for dawn/dusk times
require(maptools) # Required for dawn/dusk times

# @@@@@@@@@@@@@@@@@@@@@@@@@@@@@@@@@@@@@@@@@@@@@@@@@@
# @@@@@ Data Preparation
# @@@@@@@@@@@@@@@@@@@@@@@@@@@@@@@@@@@@@@@@@@@@@@@@@@

# Import datasets
data <- read.csv("Data/EMU-6-21/fentondata-all.csv")

# @@@@@@@@@@@@@@@@@@@@@@@@@@@@@@@@@@@@@@@@@@@@@@@@@@
# @@@@@ ggPlot Theme
# @@@@@@@@@@@@@@@@@@@@@@@@@@@@@@@@@@@@@@@@@@@@@@@@@@

ggplot.theme <- theme(
    
    # Text size for axis ticks
    axis.text.y = element_text(size = 14),
    axis.text.x = element_text(size = 14),
    
    # Text size for axis labels
    # Also move them away from the axes a bit for more space
    axis.title.x = element_text(size = 18, face = "bold", vjust = -1),
    axis.title.y = element_text(size = 18, face = "bold", vjust = 1.5),
    
    # Plot title size
    plot.title = element_text(size = 20, face = "bold"),
    
    # Margins for top, right, bottom, left
    plot.margin = grid::unit(c(1.5, 1.5, 1.5, 1.2), "lines"), 
    
    # Legend text size
    legend.text = element_text(size = 14),
    legend.text.align = 0, 
    legend.title = element_text(size = 16, face = "bold"),
    legend.key.size = grid::unit(1.4, "line"),
    legend.key = element_blank()
    )

```

```{r 'Data_Wrangling', echo = F, include = F}

# Data wrangling on the main dataset
data <- data %>%
    
    # Convert the timestamp to a date/time object
    mutate(timestamp = as.POSIXct(timestamp)) %>%
    
    # Remove the seconds from the time, leaving only hour/minute
    mutate(timestamp = timestamp - second(timestamp))

# Take a look at the structure of the main dataset
str(data)

# Convert the dataset to wide format 
data.wide <- data %>%

    # Go to pure long format: all measurements in one column
    gather(measurement, value, temperature, humidity, vwc, 
        pfd, light, soil, pressure) %>%
    
    # Make a column that is both source & measurement type
    unite(measure, source, measurement) %>%
    
    # Get rid of columns that aren't needed
    # Or won't work with wide format
    select(-site, -voltage, -type, -emu) %>%
    
    # Filter out the rows where the value is NA 
    filter(!is.na(value)) %>%
    
    # Go from long format to wide: each row is a site at one time
    spread(measure, value)

# Take a look at the structure of the wide dataset
str(data.wide)

# Dawn/Dusk times dataset
# See: http://rstudio-pubs-static.s3.amazonaws.com/17282_9510673f07294de7905e11c7f2b043a5.html

# Create a coordinate for the Fenton site
fenton.coord <- matrix(c(-72.238159, 41.825076), nrow = 1) %>%
    SpatialPoints(proj4string = CRS("+proj=longlat +datum=WGS84"))

# Create a data frame with dawn and dusk times with the following start/end dates for the project
darkness <- data.frame(date = seq(from = as.POSIXct("2017-05-30"), 
     to = as.POSIXct("2017-06-21"), by = "day")) %>%
     
     # Add dawn times
     mutate(dawn.time = crepuscule(fenton.coord, date, solarDep = 6, 
         direction = "dawn", POSIXct.out = TRUE)$time) %>%
  
     # Add dusk times
     mutate(dusk.time = crepuscule(fenton.coord, date, solarDep = 6, 
         direction = "dusk", POSIXct.out = TRUE)$time) %>%
    
     # Convert dawn and dusk times to hours since the start
     mutate(
         dusk = round(interval(as.POSIXct("2017-05-30 12:00"), lag(dusk.time)) /
            dhours(1)),
         dawn = round(interval(as.POSIXct("2017-05-30 12:00"), dawn.time) /
            dhours(1))) %>%
    
    # Get rid of the first day
    filter(date >= as.POSIXct("2017-05-31"))

diff.darkness <- rbind(
    darkness %>% mutate(measurement = "Temperature", ymin = -14, ymax = 8), 
    darkness %>% mutate(measurement = "Humidity", ymin = -26, ymax = 37), 
    darkness %>% mutate(measurement = "PFD", ymin = -1665, ymax = 10),
    darkness %>% mutate(measurement = "VWC", ymin = -0.18, ymax = 0)) %>%
    
    # Order the measurements
    mutate(measurement = factor(measurement, 
        levels = c("Temperature", "Humidity", "PFD", "VWC")))

```

### Temperature

Differences in temperature between EMUs relative to Hobo Pendants at all positions in the transects.

Hobos tend to read high, especially during the day.  Strongly suggests heat trapped from sun.

```{r 'Temp_Diff_Hobo', echo = F}

# Set ymin and ymax limits separately for the two transects
temp.hobo.darkness <- rbind(
    darkness %>% mutate(transect = "Meadow", ymin = -6, ymax = 10),
    darkness %>% mutate(transect = "Woods", ymin = -4, ymax = 4))

# Plot relative differences in temperature
data.wide %>%
    
    # Make columns for differences between Hobo & EMU
    mutate(Hobo_diff = Hobo_temperature - EMU_temperature) %>%
    
    # Get rid of missing data rows
    filter(!is.na(Hobo_diff)) %>%
    
    # Plot differences over time
    ggplot(aes(x = hour, y = Hobo_diff)) +
    
        # Make a facet for each transect
        facet_wrap(~ transect, ncol = 1, scales = "free_y") + 
    
        # Add rectangles for darkness
        geom_rect(data = temp.hobo.darkness, aes(xmin = dusk, xmax = dawn, 
            ymin = ymin, ymax = ymax, x = NULL, y = NULL, color = NULL), 
            fill = "grey85", show.legend = F) + 
    
        # Add points
        geom_point(alpha = 0.3) +
    
        # Add horizontal line at zero
        geom_hline(yintercept = 0, color = "red") + 
    
        # Add axis labels
        xlab("Hour") + 
        ylab("Temperature Difference (ºC)") + 
    
        # Title
        ggtitle("Hobo Temperature Difference") +
    
        # Add theme
        ggplot.theme

```

Differences in temperature between EMUs relative to iButtons at the first position of each transect.

Prior to hour 98, the iButtons had fallen on the ground, so you are seeing the difference between ground temperature and that of 10 cm above.

There is minimal difference in temperature between the iButtons and Hobos on both transects from hour 98 to 190.  After 190, the meadow BME280 started failing. Subsequent values may be inaccurate.

```{r 'Temp_Diff_iButton', echo = F}

# Set ymin and ymax limits separately for the two transects
temp.iButton.darkness <- rbind(
    darkness %>% mutate(transect = "Meadow", ymin = -8, ymax = 16),
    darkness %>% mutate(transect = "Woods", ymin = -8, ymax = 5))

# Plot relative differences in temperature
data.wide %>%
    
    # Make a colummn for differences between iButton & EMU
    mutate(iButton_diff = iButton_temperature - EMU_temperature) %>%

    # Get rid of missing data rows
    filter(!is.na(iButton_diff)) %>%
    
    # Plot differences over time
    ggplot(aes(x = hour, y = iButton_diff)) +
    
        # Make a facet for each transect
        facet_wrap(~ transect, ncol = 1, scales = "free_y") + 
    
        # Add rectangles for darkness
        geom_rect(data = temp.iButton.darkness, aes(xmin = dusk, xmax = dawn, 
            ymin = ymin, ymax = ymax, x = NULL, y = NULL, color = NULL), 
            fill = "grey85", show.legend = F) + 
    
        # Add points
        geom_point(alpha = 0.3) +
    
        # Add horizontal line at zero
        geom_hline(yintercept = 0, color = "red") + 

        # Add axis labels
        xlab("Hour") + 
        ylab("Temperature Difference (ºC)") + 
    
        # Title
        ggtitle("iButton Temperature Difference") +
    
        # Add theme
        ggplot.theme

```

### Humidity

Differences in humidity between EMUs relative to iButtons at the first position of each transect.

Prior to hour 98, the iButtons had fallen on the ground, so this is the difference between ground temperature and that of 10 cm above.

It looks like humidity is lower during the day with the iButton on the meadow transect, and generally higher at all times in the woods.

```{r 'Humid_Diff', echo = F}

# Set ymin and ymax limits separately for the two transects
humid.darkness <- rbind(
    darkness %>% mutate(transect = "Meadow", ymin = -36, ymax = 55),
    darkness %>% mutate(transect = "Woods", ymin = -12, ymax = 72))

# Plot relative differences in humidity
data.wide %>%
    
    # Only include data from the first site on a transect
    #filter(order == 1, hour > 98) %>%
    
    # Make a colummn for differences between iButton & EMU
    mutate(iButton_diff = iButton_humidity - EMU_humidity) %>%

    # Get rid of missing data rows
    filter(!is.na(iButton_diff)) %>%
    
    # Plot differences over time
    ggplot(aes(x = hour, y = iButton_diff)) +
    
        # Make a facet for each transect
        facet_wrap(~ transect, ncol = 1, scales = "free_y") + 

        # Add rectangles for darkness
        geom_rect(data = humid.darkness, aes(xmin = dusk, xmax = dawn, 
            ymin = ymin, ymax = ymax, x = NULL, y = NULL, color = NULL), 
            fill = "grey85", show.legend = F) + 
    
        # Add points
        geom_point(alpha = 0.3) +
    
        # Add horizontal line at zero
        geom_hline(yintercept = 0, color = "red") + 
    
        # Theme the legend
        scale_color_manual(name = "Difference", values = c("blue")) + 
    
        # Add axis labels
        xlab("Date") + 
        ylab("Relative Humidity (%)") + 
    
        # Title
        ggtitle("iButton Humidity Difference") +
    
        # Add theme
        ggplot.theme

```

## Comparisons between EMU & iButton/Hobo Pendant for Woods transect

The Hobo Pendant reads slightly high on temperature (by about 2ºC).  Presumably it's getting heated inside of its enclosed case.

```{r 'Temp_Comp_Hobo', echo = F, fig.width=10}
    
# Plot relative differences in temperature
data.wide %>%
    
    # Get rid of the first position in the meadow transect
    filter(!is.na(EMU_temperature), !(transect == "Meadow" & order == 1)) %>%
    
    # Plot differences over time
    ggplot(aes(y = EMU_temperature, x = Hobo_temperature)) +
    
        # Make a facet for each transect
        facet_wrap(~ transect, ncol = 2) + 
    
        # Add points
        geom_point(color = "blue", alpha = 0.6) +
    
        # Add horizontal line at zero
        geom_abline(intercept = 0, slope = 1) + 
    
        # Add linear model
        geom_smooth(method = "lm", color = "red", se = F) + 
    
        # Add the equation
        stat_poly_eq(aes(label = ..eq.label..),
               eq.x.rhs = "italic(x)", coef.digits = 3, label.x = 15, 
               label.y = 40, parse = T, size = 7,
               formula = y ~ x) +
        
        # Add the R^2
        stat_poly_eq(aes(label = ..rr.label..),
               rr.digits = 3, label.x = 15, label.y = 36,
               parse = T, size = 7, formula = y ~ x) +
    
        # Add horizontal line at zero
        geom_abline(intercept = 0, slope = 1) + 
    
        # Add axis labels
        xlab("Hobo Temperature (ºC)") + 
        ylab("EMU Temperature (ºC)") + 
    
        # Add theme
        ggplot.theme

# Combine transects into one graph
hobo.temp <- data.wide %>%
    
    # Get rid of the first position in the meadow transect
    filter(!is.na(EMU_temperature), !(transect == "Meadow" & order == 1)) %>%
    
    # Plot differences over time
    ggplot(aes(y = EMU_temperature, x = Hobo_temperature)) +
    
        # Add points
        geom_point(color = "blue", alpha = 0.6) +
    
        # Add horizontal line at zero
        geom_abline(intercept = 0, slope = 1) + 
    
        # Add linear model
        geom_smooth(method = "lm", color = "red", se = F) + 
    
        # Add the equation
        stat_poly_eq(aes(label = ..eq.label..),
               eq.x.rhs = "italic(x)", coef.digits = 3, label.x = 15, 
               label.y = 46, parse = T, size = 7,
               formula = y ~ x) +
        
        # Add the R^2
        stat_poly_eq(aes(label = ..rr.label..),
               rr.digits = 3, label.x = 15, label.y = 40,
               parse = T, size = 7, formula = y ~ x) +
    
        # Add horizontal line at zero
        geom_abline(intercept = 0, slope = 1) + 
    
        # Add axis labels
        xlab("Hobo Temperature (ºC)") + 
        ylab("EMU Temperature (ºC)") + 
    
        # Add theme
        ggplot.theme

```

The iButtons read slightly lower than the EMU when it's cold, and slightly higher when hot.  Presumably, this is in response to the metal enclosure.

```{r 'Temp_Comp_iButton', echo = F, fig.width=10}

# Plot relative differences in temperature
data.wide %>%
    
    # Only show the woods transect at the first site
    filter(order == 1, hour > 98, 
        !is.na(EMU_temperature), !is.na(iButton_temperature)) %>%
    
    # Plot differences over time
    ggplot(aes(y = EMU_temperature, x = iButton_temperature)) +

        # Make a facet for each transect
        facet_wrap(~ transect, ncol = 2) + 
    
        # Add points
        geom_point(color = "blue", alpha = 0.6) +
    
        # Add horizontal line at zero
        geom_abline(intercept = 0, slope = 1) + 
    
        # Add linear model
        geom_smooth(method = "lm", color = "red", se = F) + 
    
        # Add the equation
        stat_poly_eq(aes(label = ..eq.label..),
               eq.x.rhs = "italic(x)", coef.digits = 4, label.x = 15, 
               label.y = 40, parse = T, size = 7,
               formula = y ~ x) +
        
        # Add the R^2
        stat_poly_eq(aes(label = ..rr.label..),
               rr.digits = 3, label.x = 15, label.y = 36,
               parse = T, size = 7, formula = y ~ x) +
    
        # Add horizontal line at zero
        geom_abline(intercept = 0, slope = 1) + 
    
        # Theme the legend
        #scale_color_manual(name = "Difference", values = c(2, 3)) + 
    
        # Add axis labels
        xlab("iButton Temperature (ºC)") + 
        ylab("EMU Temperature (ºC)") + 
    
        # Add theme
        ggplot.theme

# Plot relative differences in temperature
ibutton.temp <- data.wide %>%
    
    # Only show the woods transect at the first position after hour 98
    filter(!is.na(EMU_temperature), !is.na(iButton_temperature), 
           order == 1, hour > 98, transect != "Meadow") %>%
    
    # Plot differences over time
    ggplot(aes(y = EMU_temperature, x = iButton_temperature)) +
    
        # Add points
        geom_point(color = "blue", alpha = 0.6) +
    
        # Add horizontal line at zero
        geom_abline(intercept = 0, slope = 1) + 
    
        # Add linear model
        geom_smooth(method = "lm", color = "red", se = F) + 
    
        # Add the equation
        stat_poly_eq(aes(label = ..eq.label..),
               eq.x.rhs = "italic(x)", coef.digits = 4, label.x = 16.5, 
               label.y = 32, parse = T, size = 7,
               formula = y ~ x) +
        
        # Add the R^2
        stat_poly_eq(aes(label = ..rr.label..),
               rr.digits = 3, label.x = 16.5, label.y = 29,
               parse = T, size = 7, formula = y ~ x) +
    
        # Add horizontal line at zero
        geom_abline(intercept = 0, slope = 1) + 
    
        # Theme the legend
        #scale_color_manual(name = "Difference", values = c(2, 3)) + 
    
        # Add axis labels
        xlab("iButton Temperature (ºC)") + 
        ylab("EMU Temperature (ºC)") + 
    
        # Add theme
        ggplot.theme

```

Comparing iButtons to Hobos, we see that hobos read too high for anything over about 10C.  Again evidence of self-heating.

```{r 'Temp_Comp_iButton_Hobo', echo = F, fig.width=10}

# Plot relative differences in temperature between Hobos and iButtons
hobo.ibutton.temp <- data.wide %>%
    
    # Only show the first position after hour 98 (when iButtons fixed)
    filter(!is.na(Hobo_temperature), !is.na(iButton_temperature), 
           order == 1, hour > 98) %>%
    
    # Plot differences over time
    ggplot(aes(y = Hobo_temperature, x = iButton_temperature)) +
    
        # Add points
        geom_point(color = "blue", alpha = 0.6) +
    
        # Add horizontal line at zero
        geom_abline(intercept = 0, slope = 1) + 
    
        # Add linear model
        geom_smooth(method = "lm", color = "red", se = F) + 
    
        # Add the equation
        stat_poly_eq(aes(label = ..eq.label..),
               eq.x.rhs = "italic(x)", coef.digits = 4, label.x = 13, 
               label.y = 44, parse = T, size = 7,
               formula = y ~ x) +
        
        # Add the R^2
        stat_poly_eq(aes(label = ..rr.label..),
               rr.digits = 3, label.x = 13, label.y = 38,
               parse = T, size = 7, formula = y ~ x) +
    
        # Add horizontal line at zero
        geom_abline(intercept = 0, slope = 1) + 
    
        # Theme the legend
        #scale_color_manual(name = "Difference", values = c(2, 3)) + 
    
        # Add axis labels
        xlab("iButton Temperature (ºC)") + 
        ylab("Hobo Temperature (ºC)") + 
    
        # Add theme
        ggplot.theme

# Display
hobo.ibutton.temp

```

### Humidity

The iButtons have slightly higher humidity (3-5% or so) in the Woods.  They also can return values higher than 100%.  

In the meadow, the BME280 failed, and I think all the humidity values are bogus.

```{r 'Humid_Comp', echo = F, fig.width=10}

# Plot relative differences in humidity
data.wide %>%

    # Only show the woods transect at the first position after hour 98
    filter(!is.na(EMU_humidity), !is.na(iButton_humidity), 
           order == 1, hour > 98) %>%
    
    # Plot differences over time
    ggplot(aes(x = iButton_humidity, y = EMU_humidity)) +

        # Make a facet for each transect
        facet_wrap(~ transect, ncol = 2) + 

        # Add points
        geom_point(color = "blue", alpha = 0.6) +
    
        # Add horizontal line at zero
        geom_abline(intercept = 0, slope = 1) + 

        # Add linear model
        geom_smooth(method = "lm", color = "red", se = F) + 
    
        # Add the equation
        stat_poly_eq(aes(label = ..eq.label..),
               eq.x.rhs = "italic(x)", coef.digits = 4, label.x = 50, 
               label.y = 100, parse = T, size = 7,
               formula = y ~ x) +
        
        # Add the R^2
        stat_poly_eq(aes(label = ..rr.label..),
               rr.digits = 3, label.x = 50, label.y = 95,
               parse = T, size = 7, formula = y ~ x) +
    
        # Theme the legend
        #scale_color_manual(name = "Difference", values = c(2, 3)) + 
    
        # Add axis labels
        xlab("iButton Humidity (%)") + 
        ylab("EMU Humidity (%)") + 
    
        # Add theme
        ggplot.theme

# Plot relative differences in humidity
ibutton.humid <- data.wide %>%

    # Only show the woods transect at the first position after hour 98
    filter(!is.na(EMU_humidity), !is.na(iButton_humidity), 
           order == 1, hour > 98, transect != "Meadow") %>%
    
    # Plot differences over time
    ggplot(aes(x = iButton_humidity, y = EMU_humidity)) +

        # Add points
        geom_point(color = "blue", alpha = 0.6) +
    
        # Add horizontal line at zero
        geom_abline(intercept = 0, slope = 1) + 

        # Add linear model
        geom_smooth(method = "lm", color = "red", se = F) + 
    
        # Add the equation
        stat_poly_eq(aes(label = ..eq.label..),
               eq.x.rhs = "italic(x)", coef.digits = 3, label.x = 56, 
               label.y = 100, parse = T, size = 7,
               formula = y ~ x) +
        
        # Add the R^2
        stat_poly_eq(aes(label = ..rr.label..),
               rr.digits = 3, label.x = 56, label.y = 90,
               parse = T, size = 7, formula = y ~ x) +
    
        # Theme the legend
        #scale_color_manual(name = "Difference", values = c(2, 3)) + 
    
        # Add axis labels
        xlab("iButton Humidity (%)") + 
        ylab("EMU Humidity (%)") + 
    
        # Add theme
        ggplot.theme

```

```{r 'Temp_Humid_Comp', echo = F, fig.height=10, fig.width=10}

ggdraw() +
    
    # Add the four temp and humidity comparison graphs
    draw_plot(hobo.temp, 0, 0.49, 0.5, 0.49) +
    draw_plot(ibutton.temp, 0.5, 0.49, 0.5, 0.49) +
    draw_plot(hobo.ibutton.temp, 0.5, 0, 0.5, 0.49) +
    draw_plot(ibutton.humid, 0, 0, 0.5, 0.49) + 
    
    # Add subplot labels
    draw_plot_label(c("A", "B", "C", "D"), 
        x = c(0.01, 0.51, 0.01, 0.51), 
        y = c(1, 1, 0.51, 0.51), size = 24)

```

### Session Information

```{r 'Session_Info', echo = F, comment = ""}

# Add session information to help with reproduceability
sessionInfo()

```

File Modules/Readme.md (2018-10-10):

# Lua Modules

The following are Lua modules we have written that are not incorporated in NodeMCU firmware. They function as libraries, allowing the EMU code to import functionality or talk to sensors, with minimal programming on the part of the user.

## Modules

* [ads1115](/Modules/ads1115/) - Analog to digital converter module for soil moisture
* [bh17150](/Modules/bh1750/) - Lux sensor module for PFD
* [csv](/Modules/csv/) - CSV module for writing data files
* [ds3231](/Modules/ds3231/) - Clock module for keeping time and waking up the EMU to measure
* [logging](/Modules/logging/) - Logging module to for keeping a log file in addition to the data file

For the EMU code to work, all five of these modules must also be uploaded to the EMU.  We also recommend [compiling them](https://nodemcu.readthedocs.io/en/dev/en/modules/node/#nodecompile) to .lc files and removing the original .lua source files, so that they take up less space and RAM while being used. You can do this in ESPlorer or via a handy [compile script](/Useful%20Scripts/module-compiler.lua)

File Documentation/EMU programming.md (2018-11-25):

# Programming EMUs

Programming an EMU requires two steps
1. the D1 Mini must have a firmware operating system flashed to it
2. Our code must be uploaded, generally using ESplorer

## Flashing the firmware

Using nodemcu-pyuploader or esptool (see [Computer setup](Computer%20setup.md)), flash the firmware to the D1 Mini while connected to the computer. See the [firmware flashing instructions](/Firmware) for more details.

Note: Sometimes a D1 Mini is not able to set itself in firmware flashing mode when connected to the rest of the EMU.  We recommend taking it off the breadboard first. You can also force it into firmware-flashing mode by connecting pin D3 to GND and pressing the reset switch. Remove the connection when finished.

## Connecting to the EMU with ESPlorer

1. Click the blue circle-arrow button at the top right side of ESPlorer.  This refreshes the list of available serial/COM ports
2. Select the COM port that corresponds to the connected EMU (see [Computer setup](/Documentation/Computer%20setup.md)) for how to identify which one this is. 
3. Ensure that the baud/connection speed beside the Open button is set to 115200
4. Click open.  You may have to reset the EMU (press the tiny button beside the USP connector) for any output to show up on the screen
5. Note: if the EMU already has code on it, that code will begin to run when you reset the EMU.  In that case, click the Abort Snippet button below the commandline output (this needs to be set up manually, [Computer setup](/Documentation/Computer%20setup.md)), or connect a wire between D7 and Ground.

Once these steps are completed, you are connected to the EMU.  You can run code directly by typing it in the box at the bottom right of the ESPlorer window and clicking Send.  Or, you can open or create a script file in the left pane, type code in there, and send it to the EMU using the Block or Line buttons below the Settings tab.  You can send a whole script file to the EMU for execution using the Send to ESP button, or upload a file using the Save to ESP or Upload buttons.

## Uploading Code

The software to run an EMU consists of [Modules](/Modules/), libraries that we have written to interface with sensors or write out data, a script that takes measurements from all the sensors, and a startup system.  All of the following files need to be uploaded to an EMU in order for it to work correctly.  We recommend uploading them in the order they appear below to minimize problems.

**[Modules](/Modules/)**
* [ads1115](/Modules/ads1115/) - Analog to digital converter module for soil moisture
* [bh1750](/Modules/bh1750/) - Lux sensor module for PFD
* [csv](/Modules/csv/) - CSV module for writing data files
* [ds3231](/Modules/ds3231/) - Clock module for keeping time and waking up the EMU to measure
* [logging](/Modules/logging/) - Logging module to for keeping a log file in addition to the data file

After you have uploaded a module, compile it by clicking the Save&Compile button or by running `node.compile("modulename.lua")`.  You can then delete the .lua file

**[EMU-Software](/EMU-Software/)**
* [config.lua](/EMU-Software/config.lua) - This script just sets a few configuration variables that are available for the main script.  We use it to set the time interval for measurements, the timezone, logging verbosity, and the data and log filenames for each EMU. This should be customized for each EMU.
* [init.lua](/EMU-Software/init.lua) - This is a special script, that if present, is run by default by the firmware.  Ours is carefully written to prevent errors and to give the user some ways to exit the code in case there is a problem (connecting D7 to ground or setting abort=1).  Without these failsafes, code could crash, restart, and crash again endlessly, requiring a new firmware. Note: An easy way to set abort=1 is provided by editing a snippet in Esplorer, to make an Abort button (see [Computer setup](Computer%20setup.md)).
* [measure.lua](/EMU-Software/measure.lua) - This script does all the work of taking a measurement: reading the sensors and logging the data

The init.lua file should not be compiled.  The other two scripts: config.lua and measure.lua are assumed to not be compiled, though they could be.  One would just need to change the name to .lc where they are loaded in init.lua and config.lua respectively.

Once all code is uploaded, and the D1 Mini is connected to the EMU breadboard, resetting the D1 Mini should result in it taking a measurement.  If logging is enabled, there should be output shown on the command prompt of ESPlorer

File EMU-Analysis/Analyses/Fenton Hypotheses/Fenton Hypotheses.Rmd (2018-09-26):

---
title: "Analysis of Fenton Hypotheses"
author: "James Mickley"
output:
  html_document:
    keep_md: yes
    theme: readable
  html_notebook:
    fig_caption: yes
    theme: readable
graphics: yes
editor_options: 
  chunk_output_type: console
---

```{r setup, include = F}
# @@@@@@@@@@@@@@@@@@@@@@@@@@@@@@@@@@@@@@@@@@@@@@@@@@
# @@@@@ Knitr Options
# @@@@@@@@@@@@@@@@@@@@@@@@@@@@@@@@@@@@@@@@@@@@@@@@@@

# Set root directory to the project directory
knitr::opts_knit$set(root.dir = rprojroot::find_rstudio_root_file())

# Set default knitr options: 
# Suppress warnings and messages, cache chunks, 
#  set default figure size to 6x8 at 300 dpi, and save a png and pdf
knitr::opts_chunk$set(warning = F, message = F, collapse = T, cache = T,
    fig.height = 6, fig.width = 8, dpi = 300, # 6x8" @ 300dpi:1800x2400=4.3MP
    dev = c('png', 'pdf'), dev.args = list(pdf = list(onefile = F)))

```

### Overview

We set up a number of expectations for the Fenton site

1. The temperature should be lower in the woods
2. The humidity should be higher in the woods
3. The light levels should be lower in the woods
4. Soil moisture should show a gradient in both transects
    a. The woods should have a gradient from top to bottom of hill
    b. The meadow should have a gradient from the meadow to the swamp

```{r 'Main_Code', include = F}

# @@@@@@@@@@@@@@@@@@@@@@@@@@@@@@@@@@@@@@@@@@@@@@@@@@
# @@@@@ Setup - This code is run, but output is hidden
# @@@@@@@@@@@@@@@@@@@@@@@@@@@@@@@@@@@@@@@@@@@@@@@@@@

# Load Packages
require(tidyverse) # Needed for data wrangling
require(cowplot) # Needed for publication-quality ggplots
require(rgeos) # Required for dawn/dusk times
require(maptools) # Required for dawn/dusk times
require(knitr) # Needed to print tables to markdown
require(lubridate) # Needed for working with dates

# @@@@@@@@@@@@@@@@@@@@@@@@@@@@@@@@@@@@@@@@@@@@@@@@@@
# @@@@@ Data Preparation
# @@@@@@@@@@@@@@@@@@@@@@@@@@@@@@@@@@@@@@@@@@@@@@@@@@

# Import datasets
data <- read.csv("Data/EMU-6-21/fentondata-all.csv")

# @@@@@@@@@@@@@@@@@@@@@@@@@@@@@@@@@@@@@@@@@@@@@@@@@@
# @@@@@ ggPlot Theme
# @@@@@@@@@@@@@@@@@@@@@@@@@@@@@@@@@@@@@@@@@@@@@@@@@@

ggplot.theme <- theme(
    
    # Text size for axis ticks
    axis.text.y = element_text(size = 14),
    axis.text.x = element_text(size = 14),
    
    # Text size for axis labels
    # Also move them away from the axes a bit for more space
    axis.title.x = element_text(size = 18, face = "bold", vjust = -1),
    axis.title.y = element_text(size = 18, face = "bold", vjust = 1.5),
    
    # Plot title size
    plot.title = element_text(size = 20, face = "bold"),
    
    # Margins for top, right, bottom, left
    plot.margin = grid::unit(c(1.5, 1.5, 1.5, 1.2), "lines"), 
    
    # Legend text size
    legend.text = element_text(size = 14),
    legend.text.align = 0, 
    legend.title = element_text(size = 16, face = "bold"),
    legend.key.size = grid::unit(1.4, "line"),
    legend.key = element_blank()
    )

```

```{r 'Data_Wrangling', echo = F, include = F}

# Data wrangling on the main dataset
fenton <- data %>%
    
    # Convert the timestamp to a date/time object
    mutate(timestamp = as.POSIXct(timestamp)) %>%
    
    # Remove the seconds from the time, leaving only hour/minute
    mutate(timestamp = timestamp - second(timestamp))

# Take a look at the structure of the main dataset
str(fenton)

# Convert the dataset to wide format 
fenton.wide <- fenton %>%

    # Go to pure long format: all measurements in one column
    gather(measurement, value, temperature, humidity, vwc, 
        pfd, light, soil, pressure) %>%
    
    # Make a column that is both source & measurement type
    unite(measure, source, measurement) %>%
    
    # Get rid of columns that aren't needed
    # Or won't work with wide format
    select(-site, -voltage, -type, -emu) %>%
    
    # Filter out the rows where the value is NA 
    filter(!is.na(value)) %>%
    
    # Go from long format to wide: each row is a site at one time
    spread(measure, value)

# Take a look at the structure of the wide dataset
str(fenton.wide)

# Calculate hourly means and differences between 2 transects @ Fentonb
diff <- fenton %>%
    
    filter(source == "EMU") %>%

    # Group by transect and each hour separately
    group_by(hour, transect) %>%
    
    # Calculate mean and variance by hour for each transect
    mutate(t.mean = mean(temperature, na.rm = T), 
        t.var = var(temperature, na.rm = T), 
        t.obs = sum(!is.na(temperature)),
        h.mean = mean(humidity, na.rm = T), 
        h.var = var(humidity, na.rm = T), 
        h.obs = sum(!is.na(humidity)),
        l.mean = mean(pfd, na.rm = T), 
        l.var = mean(pfd, na.rm = T), 
        l.obs = sum(!is.na(pfd)),
        s.mean = mean(vwc, na.rm = T), 
        s.var = mean(vwc, na.rm = T), 
        s.obs = sum(!is.na(vwc))        
        ) %>%
    
    # Group by hour alone
    group_by(hour) %>%
    
    # Calculate difference between fenton woods and meadow for each hour
    # Also calculate standard error of differences between means & 95% conf.int
    # http://onlinestatbook.com/2/sampling_distributions/samplingdist_diff_means.html
    # http://stattrek.com/estimation/difference-in-means.aspx?Tutorial=AP
    mutate(t.diff = t.mean - t.mean[transect == "Meadow"][1], 
        t.vn = t.var / t.obs,
        t.stderr = sqrt(t.vn + t.vn[transect == "Meadow"][1]), 
        t.conf = t.stderr * 1.96,
        
        h.diff = h.mean - h.mean[transect == "Meadow"][1], 
        h.vn = h.var / h.obs,
        h.stderr = sqrt(h.vn + h.vn[transect == "Meadow"][1]), 
        h.conf = h.stderr * 1.96,
        
        l.diff = l.mean - l.mean[transect == "Meadow"][1], 
        l.vn = l.var / l.obs,
        l.stderr = sqrt(l.vn + l.vn[transect == "Meadow"][1]), 
        l.conf = l.stderr * 1.96, 
        
        s.diff = s.mean - s.mean[transect == "Meadow"][1], 
        s.vn = s.var / s.obs,
        s.stderr = sqrt(s.vn + s.vn[transect == "Meadow"][1]), 
        s.conf = s.stderr * 1.96
        
        ) %>%
    
    # Group by only the variables needed and summarize
    group_by(transect, day, hour, day.hr, 
        t.mean, t.diff, t.stderr, t.conf, 
        h.mean, h.diff, h.stderr, h.conf, 
        l.mean, l.diff, l.stderr, l.conf, 
        s.mean, s.diff, s.stderr, s.conf) %>%
    
    # Summarize by transect & hour
    summarize %>%
    
    # Convert back to normal data frame
    data.frame

# Create a new dataset with just diff & conf.int
diff.long <- diff %>% 
    
    # Only include the woods, since differences will be zero @ Meadow (reference pt)
    filter(transect == "Woods") %>%
    
    # Get rid of unneeded columns
    select(-t.mean, -h.mean, -l.mean, s.mean, 
           -t.stderr, -h.stderr, -l.stderr, s.stderr) %>%
    
    # Gather diff and conf columns into variable & value columns
    gather(variable, value, ends_with("diff"), ends_with("conf")) %>%
    
    # Split the variable column into measurement and variable
    separate(variable, into = c('measurement','var')) %>%
    
    # Spread the variable & value columns back into diff and conf cols
    spread(var, value) %>%
    
    # Recode t, h, and l, into their measurement names
    mutate(measurement = factor(recode(measurement, 
        "t" = "Temperature", "h" = "Humidity", "l" = "PFD", "s" = "VWC"), 
        levels = c("Temperature", "Humidity", "PFD", "VWC"))) 

# Make a mean volumetric water content by hour/emu dataset
soil.hr <- fenton %>%

    # Group by emu and hour
    group_by(transect, emu, order, day, hour, day.hr) %>%
    
    # Summarize means and standard errors for each emu by hour
    summarize(mean = mean(vwc), stderr = sd(vwc) / sqrt(n())) %>%
    
    # Convert to normal data frame
    data.frame

# Dawn/Dusk times dataset
# See: http://rstudio-pubs-static.s3.amazonaws.com/17282_9510673f07294de7905e11c7f2b043a5.html

# Create a coordinate for the Fenton site
fenton.coord <- matrix(c(-72.238159, 41.825076), nrow = 1) %>%
    SpatialPoints(proj4string = CRS("+proj=longlat +datum=WGS84"))

# Create a data frame with dawn and dusk times with the following start/end dates for the project
darkness <- data.frame(date = seq(from = as.POSIXct("2017-05-30"), 
     to = as.POSIXct("2017-06-21"), by = "day")) %>%
     
     # Add dawn times
     mutate(dawn.time = crepuscule(fenton.coord, date, solarDep = 6, 
         direction = "dawn", POSIXct.out = TRUE)$time) %>%
  
     # Add dusk times
     mutate(dusk.time = crepuscule(fenton.coord, date, solarDep = 6, 
         direction = "dusk", POSIXct.out = TRUE)$time) %>%
    
     # Convert dawn and dusk times to hours since the start
     mutate(
         dusk = round(interval(as.POSIXct("2017-05-30 12:00"), lag(dusk.time)) /
            dhours(1)),
         dawn = round(interval(as.POSIXct("2017-05-30 12:00"), dawn.time) /
            dhours(1))) %>%
    
    # Get rid of the first day
    filter(date >= as.POSIXct("2017-05-31"))

diff.darkness <- rbind(
    darkness %>% mutate(measurement = "Temperature", ymin = -14, ymax = 8), 
    darkness %>% mutate(measurement = "Humidity", ymin = -26, ymax = 37), 
    darkness %>% mutate(measurement = "PFD", ymin = -1665, ymax = 10),
    darkness %>% mutate(measurement = "VWC", ymin = -0.18, ymax = 0)) %>%
    
    # Order the measurements
    mutate(measurement = factor(measurement, 
        levels = c("Temperature", "Humidity", "PFD", "VWC")))

# Make a darkness dataset for soil moisture
soil.darkness <- darkness %>%
    mutate(ymin = 0, ymax = 0.45)

```

## Missing Data

```{r 'Missing_Data', echo = F}

# Calculate percentage of missing data by EMU
missing.data <- fenton %>%
    
    # Only use data from EMUs
    filter(source == "EMU") %>%
    
    # Select the variables to work with
    select(emu, temperature, humidity, pfd, vwc) %>%

    # Group by the EMUs
    group_by(emu) %>%
    
    # Sum up the number of logs, and calculate percent missing
    mutate(logs = n(), logs.missing = 1 - (logs/2109)) %>%
    
    # Ungroup
    ungroup %>%
    
    # Go to pure long format: all measurements in one column
    gather(measurement, value, temperature, humidity, vwc, 
        pfd) %>%
    
    # Group by emu/measurement
    group_by(emu, logs, logs.missing, measurement) %>%
    
    # Summarize the number of non-NA values
    summarize(n = sum(!is.na(value))) %>%
    
    # Group by EMU
    group_by(emu) %>%
    
    # Calculate the number of points missing
    mutate(data.missing = 1 - sum(n) / (2109*4)) %>%
    
    # Spread the measurements back out into columns
    spread(measurement, n) %>%
    
    # Select column order
    select(emu, logs, logs.missing, temperature, humidity, pfd, 
        vwc, data.missing) %>%

    # Ungroup  
    ungroup

# Add a line for totals
missing.data %>%

    # Total everything up
    summarize(emu = "Total", logs = sum(logs), 
        logs.missing = 1 - (logs/(2109*8)), 
        temperature = sum(temperature), 
        humidity = sum(humidity), 
        pfd = sum(pfd), vwc = sum(vwc), 
        data.missing = 1 - (temperature + humidity + pfd + vwc) / 
            (2109*4*8)
        ) %>%
    
    # Add to the summaries of each EMU
    rbind(missing.data, .) %>%
    
    # Roud missing data to 3 decimals
    mutate_at(c("logs.missing", "data.missing"), funs(round(.,3))) %>%
    
    # Print a markdown table
    kable(digits = 3, format = "markdown")

```

## Main Hypotheses

Hourly differences between the two transects. Dark rectangles denote night-time hours (between dusk and dawn)

```{r 'Hourly_Differences', echo = F}

# Take the long dataset
diff.long %>%

    # Graph differerences by hour
    ggplot(aes(x = hour, y = diff, color = measurement)) + 

        # Facet by measurement
        facet_wrap(~ measurement, ncol = 1, scales = "free") + 
    
        # Add rectangles for Darkness
        geom_rect(data = diff.darkness, 
            aes(xmin = dusk, xmax = dawn, ymin = ymin, ymax = ymax, 
                x = NULL, y = NULL, color = NULL), 
            fill = "gray85", show.legend = F) + 
        
        # Add the points, colored by measurement
        geom_point() + 
    
        # Add a red line at 0
        geom_hline(yintercept = 0, color = "red") + 

        # Add 95% confidence intervals as errorbars
        #geom_errorbar(aes(ymin = diff - conf, ymax = diff + conf)) + 
    
        # Add axis labels and graph title
        ylab("Relative Difference") + xlab("Hour") + 
        ggtitle("Wood Difference Relative to Meadow") + 
    
        # Add the custom theme
        ggplot.theme

```
Hourly soil moisture means for each position in the transect, colored by *a priori* expectations on dry to wet (wetter in the swampy end of the meadow transect, wetter at the bottom of the hill in the woods)

```{r 'Soil_Gradient', echo = F}

# Graph soil moisture gradients across transect
soil.hr %>%
    
    filter(!is.na(mean)) %>%

    # Graph soil moisture by hour, coloring by order in the transect
    ggplot(aes(x = hour, y = mean, color = order, group = order)) + 

        # Facet by transect
        facet_wrap(~ transect, ncol = 1) + 
    
        # Add rectangles for darkness
        geom_rect(data = soil.darkness, 
            aes(xmin = dusk, xmax = dawn, ymin = ymin, ymax = ymax, 
                x = NULL, y = NULL, color = NULL, group = NULL), 
            fill = "grey85", show.legend = F) + 
    
        # Add lines for each EMU  
        geom_point() + 
    
        # Color from red to blue
        scale_color_gradient(name = "EMU Order\nDry to Wet", 
            low = "blue", high = "red", trans = 'reverse') + 

        # Add 95% confidence intervals as errorbars
        #geom_errorbar(aes(ymin = mean - stderr, ymax = mean + stderr)) + 
    
        # Restrict to 0 - 0.4 VWC
        coord_cartesian(ylim = c(0, 0.45)) + 
    
        # Add axis labels and graph title
        ylab("Volumetric Water Content") + xlab("Hour") + 
        ggtitle("Transect Moisture Gradients") + 
    
        # Add the custom theme
        ggplot.theme

```

Hourly means for each transect

```{r 'Hourly_Means', echo = F}

# Plot hourly means for each transect and each variable
diff %>%
    
    # Selec the hourly mean columns
    select(transect, hour, t.mean, l.mean, h.mean, s.mean) %>%
    
    # Gather the mean columns into long format
    gather(measurement, mean, t.mean, l.mean, h.mean, s.mean) %>%
    
    # Recode t, h, and l, into their measurement names
    mutate(measurement = factor(recode(measurement, 
        "t.mean" = "Temp", "h.mean" = "Humidity", "l.mean" = "PFD", 
        "s.mean" = "VWC"), 
        levels = c("Temp", "Humidity", "PFD", "VWC"))) %>%

    # Plot means over time, coloring by transect
    ggplot(aes(x = hour, y = mean, color = transect)) + 
        
        # Facet by measurement
        facet_wrap(~ measurement, ncol = 1, scales = "free") + 
        
        # Add points
        geom_point() +
    
        # Add axis labels and graph title
        ylab("Mean") + xlab("Hour") + 
        ggtitle("Transect Hourly Means") + 
    
        # Add the custom theme
        ggplot.theme

```

### Session Information

```{r 'Session_Info', echo = F, comment = ""}

# Add session information to help with reproduceability
sessionInfo()

```

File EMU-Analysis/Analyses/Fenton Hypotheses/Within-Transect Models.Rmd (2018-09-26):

---
title: "Microenvironmental Differences Within Transects"
author: "James Mickley"
output:
  html_document:
    keep_md: yes
    theme: readable
    toc: yes
  html_notebook:
    theme: readable
graphics: yes
editor_options: 
  chunk_output_type: console
---

```{r setup, include = F}
# @@@@@@@@@@@@@@@@@@@@@@@@@@@@@@@@@@@@@@@@@@@@@@@@@@
# @@@@@ Knitr Options
# @@@@@@@@@@@@@@@@@@@@@@@@@@@@@@@@@@@@@@@@@@@@@@@@@@

# Set root directory to the project directory
knitr::opts_knit$set(root.dir = rprojroot::find_rstudio_root_file())

# Set default knitr options: 
# Suppress warnings and messages, cache chunks, 
#  set default figure size to 6x8 at 300 dpi, and save a png and pdf
knitr::opts_chunk$set(warning = F, message = F, collapse = T, cache = T,
    fig.height = 6, fig.width = 8, dpi = 300, # 6x8" @ 300dpi:1800x2400=4.3MP
    dev = c('png', 'pdf'), dev.args = list(pdf = list(onefile = F)))

```

## Overview

This analysis is looking for microenvironmental differences or gradients within transects.

We're using this [GAM approach](http://www.fromthebottomoftheheap.net/2014/05/09/modelling-seasonal-data-with-gam/).  In this approach, there are two smoothers.  One smoother is a cubic spline that accounts for intra-day variation.  Then a second spline is fitted to account for temporal variation that is not intra-day.  

Readings have temporal autocorrelation, therefore, we add an autoregressive moving average correlation structure (corAR1). We set the form here to account for autocorrelation separately for each transect position, treating positions as independent.  In every case, accounting for autocorrelation improves the models considerably, however, some autocorrelation is still unaccounted for.  Zuur et. al. say that it's usually not worth finding the optimal autocorrelation structure.  

After all temporal effects are accounted for, we test for differences among transect positions separately for each transect (woods and meadow) and each variable (temperature, humidity, vwc, pfd).

We do this with two models: in one the transect positions are treated as individual factors, and there is no explicit spatial trend.  In the other, transect positions are treated as a continuous variable, testing for a gradient.

**Expectations:**

1. The woods VWC should increase (wetter) from 1 to 4, moving down the hill (no, but heterogeneity)
2. The meadow VWC should increase (wetter) from 1 to 4, moving into the swamp (yes)
3. The woods temperature should get cooler from 1 to 4, moving down the hill (no)
4. There should be no difference in PFD, or in temperature @ the meadow
    1. In fact, there are slight gradients in PFD in both sites, especially the meadow
    2. No differences in temp at the meadow
5. Humidity is unclear, but perhaps it would mirror soil moisture patterns
    1. No gradient, but some heterogeneity (in the meadow)

#### Transects

* Meadow: 1 (dry, sunny, grassy) to 4 (wet, some shade from ferns and shrubs)
* Woods: 1 (highest part of hill, but not top) to 4 (bottom of hill)

```{r 'Main_Code', include = F, cache = F}

# @@@@@@@@@@@@@@@@@@@@@@@@@@@@@@@@@@@@@@@@@@@@@@@@@@
# @@@@@ Setup - This code is run, but output is hidden
# @@@@@@@@@@@@@@@@@@@@@@@@@@@@@@@@@@@@@@@@@@@@@@@@@@

# Load Packages
require(cowplot) # Needed for publication-quality ggplots
require(tidyverse) # Needed for data wrangling
require(lubridate) # Needed for date wrangling
require(mgcv) # Needed for gams
require(bbmle) # Needed for AICc
require(rgeos) # Required for dawn/dusk times
require(maptools) # Required for dawn/dusk times

# @@@@@@@@@@@@@@@@@@@@@@@@@@@@@@@@@@@@@@@@@@@@@@@@@@
# @@@@@ Data Preparation
# @@@@@@@@@@@@@@@@@@@@@@@@@@@@@@@@@@@@@@@@@@@@@@@@@@

# Import datasets
data <- read.csv("Data/EMU-6-21/fentondata-all.csv")

# @@@@@@@@@@@@@@@@@@@@@@@@@@@@@@@@@@@@@@@@@@@@@@@@@@
# @@@@@ ggPlot Theme
# @@@@@@@@@@@@@@@@@@@@@@@@@@@@@@@@@@@@@@@@@@@@@@@@@@

ggplot.theme <- theme(
    
    # Text size for axis ticks
    axis.text.y = element_text(size = 14),
    axis.text.x = element_text(size = 14),
    
    # Text size for axis labels
    # Also move them away from the axes a bit for more space
    axis.title.x = element_text(size = 18, face = "bold", vjust = -1),
    axis.title.y = element_text(size = 18, face = "bold", vjust = 1.5),
    
    # Plot title size
    plot.title = element_text(size = 20, face = "bold"),
    
    # Margins for top, right, bottom, left
    plot.margin = grid::unit(c(1.5, 1.5, 1.5, 1.2), "lines"), 
    
    # Legend text size
    legend.text = element_text(size = 14),
    legend.text.align = 0, 
    legend.title = element_text(size = 16, face = "bold"),
    legend.key.size = grid::unit(1.4, "line"),
    legend.key = element_blank()
    )

```

```{r 'Data_Wrangling', echo = F, include = F}

# Data wrangling on the main dataset
fenton <- data %>%
    
    # Convert the timestamp to a date/time object
    mutate(timestamp = as.POSIXct(timestamp)) %>%
    
    # Remove the seconds from the time, leaving only hour/minute
    mutate(timestamp = timestamp - second(timestamp))

# Take a look at the structure of the main dataset
#str(fenton)

#### Temperature #####

# Make a dataset for the meadow EMU temperatures
m.temp.data <- fenton %>%

    # Filter only EMU data with a temperature from the meadow
    filter(source == "EMU", !is.na(temperature), transect == "Meadow", order != 1)

# Make a dataset for the woods EMU temperatures
w.temp.data <- fenton %>%

    # Filter only EMU data with a temperature from the meadow
    filter(source == "EMU", !is.na(temperature), transect == "Woods")

#### Humidity #####

# Make a dataset for the meadow EMU humidity
m.humid.data <- fenton %>%

    # Filter only EMU data with a humidity from the meadow
    filter(source == "EMU", !is.na(humidity), humidity > 0, 
        transect == "Meadow", order != 1)

# Make a dataset for the woods EMU humidity
w.humid.data <- fenton %>%

    # Filter only EMU data with a humidity from the meadow
    filter(source == "EMU", !is.na(humidity), humidity > 0, 
        transect == "Woods")

#### VWC #####

# Make a dataset for the meadow EMU vwc
m.vwc.data <- fenton %>%

    # Filter only EMU data with a vwc from the meadow
    filter(source == "EMU", !is.na(vwc), transect == "Meadow")

# Make a dataset for the woods EMU vwc
w.vwc.data <- fenton %>%

    # Filter only EMU data with a vwc from the meadow
    filter(source == "EMU", !is.na(vwc), transect == "Woods") 

#### PFD #####

# Make a dataset for the meadow EMU pfd
m.pfd.data <- fenton %>%

    # Filter only EMU data with a pfd from the meadow
    filter(source == "EMU", !is.na(pfd), transect == "Meadow")

# Make a dataset for the woods EMU pfd
w.pfd.data <- fenton %>%

    # Filter only EMU data with a pfd from the meadow
    filter(source == "EMU", !is.na(pfd), transect == "Woods")

# Dawn/Dusk times dataset
# See: http://rstudio-pubs-static.s3.amazonaws.com/17282_9510673f07294de7905e11c7f2b043a5.html

# Create a coordinate for the Fenton site
fenton.coord <- matrix(c(-72.238159, 41.825076), nrow = 1) %>%
    SpatialPoints(proj4string = CRS("+proj=longlat +datum=WGS84"))

# Create a data frame with dawn and dusk times with the following start/end dates for the project
darkness <- data.frame(date = seq(from = as.POSIXct("2017-05-30"), 
     to = as.POSIXct("2017-06-21"), by = "day")) %>%
     
     # Add dawn times
     mutate(dawn.time = crepuscule(fenton.coord, date, solarDep = 6, 
         direction = "dawn", POSIXct.out = TRUE)$time) %>%
  
     # Add dusk times
     mutate(dusk.time = crepuscule(fenton.coord, date, solarDep = 6, 
         direction = "dusk", POSIXct.out = TRUE)$time) %>%
    
     # Convert dawn and dusk times to hours since the start
     mutate(
         dusk = round(interval(as.POSIXct("2017-05-30 12:00"), lag(dusk.time)) /
            dhours(1)),
         dawn = round(interval(as.POSIXct("2017-05-30 12:00"), dawn.time) /
            dhours(1))) %>%
    
    # Get rid of the first day
    filter(date >= as.POSIXct("2017-05-31"))

```

## Temperature

### Meadow Temperature

The model that includes transect order is worse than the base temporal model for meadow temperature.

There are no significant differences between position 2, 3, and 4 (1 is bad data and removed).  The maximum difference is 0.65 ºC between positions.

**NOTE:** Position two is the reference level for this model: the intercept is the temperature for position 2.

```{r 'Meadow_Temp', echo = F, comment = ""}

# Construct an uncorrelated gam with the two smoothers
m.temp.uncorr <- gamm(temperature ~  s(day.min, bs = "cc", k = 96) + 
    s(minute, k = 23, fx = T), data = m.temp.data)

##### Autocorrelation #####

# Set graphs to 1 row x 2 columns
layout(matrix(1:2, ncol = 2))

# plot of autocorrelation in variances
acf(resid(m.temp.uncorr$lme), lag.max = 96, main = "ACF")
pacf(resid(m.temp.uncorr$lme), lag.max = 96, main = "pACF")

# Reset the layout
layout(1)

# ARMA Coefficients (non negative, default = 0)
# p = autoregressive order
# q = moving average order

# p = 1, q = 0 (AR1), grouped by order
m.temp.ar1 <- gamm(temperature ~  s(day.min, bs = "cc", k = 96) + 
    s(minute, k = 23, fx = T), data = m.temp.data,
    correlation = corAR1(form = ~ 1|order))

# Compare models
AICctab(m.temp.uncorr$lme, m.temp.ar1$lme, nobs = nrow(m.temp.data))

# Show model summary
summary(m.temp.ar1$gam)

# Set graphs to 1 row x 2 columns
layout(matrix(1:2, ncol = 2))

# plot of autocorrelation in variances
acf(resid(m.temp.ar1$lme, type = "normalized"), lag.max = 96, main = "ACF")
pacf(resid(m.temp.ar1$lme, type = "normalized"), lag.max = 96, main = "pACF")

# Reset the layout
layout(1)

# Plot residuals over time
plot(m.temp.ar1$lme, resid(., type = "normalized") ~ minute)

##### Model Temporal Fit #####

# Set graphs to 1 row x 2 columns
layout(matrix(1:2, ncol = 2))

# Plot the two smoothers
plot(m.temp.ar1$gam, shade = T, residuals = T, ylab = "Temperature (º C)", 
    main = "Meadow Temp")

# Reset the layout
layout(1)

##### Transect Order #####

# Fit a model with transect order as a factor
m.temp.ar1.factor <- gamm(temperature ~  s(day.min, bs = "cc", k = 96) + 
    s(minute, k = 23, fx = T) + factor(order), 
    data = m.temp.data, correlation = corAR1(form = ~ 1|order))

# Fit a model with continuous transect order
m.temp.ar1.continuous <- gamm(temperature ~  s(day.min, bs = "cc", k = 96) + 
    s(minute, k = 23, fx = T) + order, 
    data = m.temp.data, correlation = corAR1(form = ~ 1|order))

# Test whether there are differences in temperature along the transect
AICctab(m.temp.uncorr$lme, m.temp.ar1$lme, m.temp.ar1.factor$lme, 
    m.temp.ar1.continuous$lme, nobs = nrow(m.temp.data))

# Show the summary for the transect order
summary(m.temp.ar1.factor$gam)
summary(m.temp.ar1.factor$lme)

```

### Woods Temperature

The model that includes transect order is worse than the base temporal model for woods temperature.

There are no significant differences between any of the positions relative to position 1, and a maximum difference of 0.48 ºC between positions.

```{r 'Woods_Temp', echo = F, comment = ""}

# Construct an uncorrelated gam with the two smoothers
w.temp.uncorr <- gamm(temperature ~  s(day.min, bs = "cc", k = 96) + 
    s(minute, k = 23, fx = T), data = w.temp.data)

##### Autocorrelation #####

# Set graphs to 1 row x 2 columns
layout(matrix(1:2, ncol = 2))

# plot of autocorrelation in variances
acf(resid(w.temp.uncorr$lme), lag.max = 96, main = "ACF")
pacf(resid(w.temp.uncorr$lme), lag.max = 96, main = "pACF")

# Reset the layout
layout(1)

# ARMA Coefficients (non negative, default = 0)
# p = autoregressive order
# q = moving average order
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

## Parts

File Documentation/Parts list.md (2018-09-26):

# Parts List

We buy most of our parts from AliExpress, shipped from China. This is nearly always the cheapest option, however the same or similar parts can often be sourced from eBay, Amazon, or [Adafruit](https://www.adafruit.com/). Most sellers on AliExpress, eBay, and Amazon ship from China. Shipments can take 2-4 weeks, and sometimes get lost, so allow ample time for parts to arrive.

While Chinese parts are cheap, the quality control varies. We often buy more than we need to allow for some rejects. AliExpress has especially good customer protection in the case of missing or faulty parts. Usually, there is no need to ship defective products back, you just get a refund.

Many Chinese sellers on AliExpress and elsewhere offer volume discounts for parts bought in lots of 2, 5, 10, 50, and 100.

## Required EMU parts

| &nbsp;&nbsp;&nbsp;&nbsp;&nbsp;&nbsp;&nbsp;&nbsp;&nbsp;&nbsp;&nbsp;Photo&nbsp;&nbsp;&nbsp;&nbsp;&nbsp;&nbsp;&nbsp;&nbsp;&nbsp;&nbsp;&nbsp; | &nbsp;&nbsp;&nbsp;&nbsp;&nbsp;&nbsp;&nbsp;&nbsp;&nbsp;&nbsp;&nbsp;&nbsp;Part&nbsp;&nbsp;&nbsp;&nbsp;&nbsp;&nbsp;&nbsp;&nbsp;&nbsp;&nbsp;&nbsp;&nbsp;&nbsp; | Number | Cost | Source | Datasheet | Notes |
| :---: | :--- | :---: | :---: | :---: | :---: | :--- | 
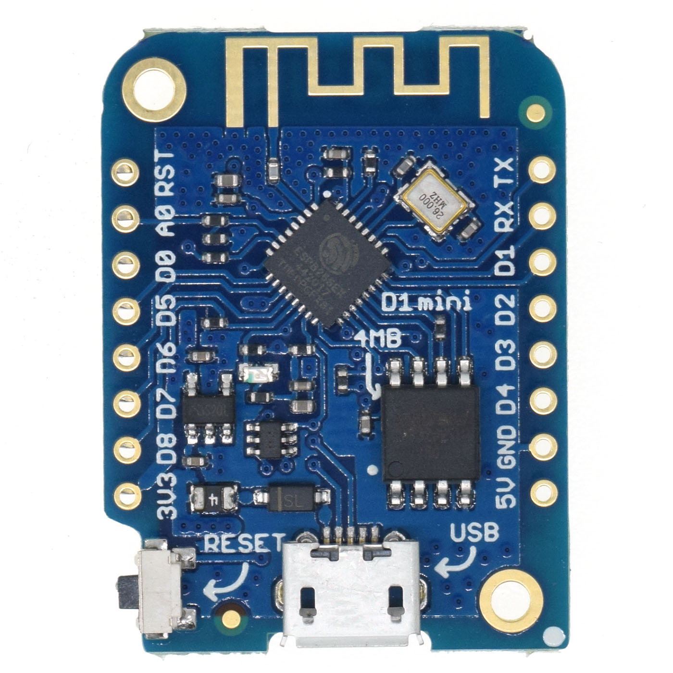
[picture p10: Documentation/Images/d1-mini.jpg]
|  | [Lolin (formerly WeMos)](https://www.wemos.cc/) D1 Mini ESP8266 | 1 | $4.50 | [AliExpress](https://www.aliexpress.com/store/product/D1-mini-Mini-NodeMcu-4M-bytes-Lua-WIFI-Internet-of-Things-development-board-based-ESP8266/1331105_32529101036.html) | [Datasheet](https://wiki.wemos.cc/products:d1:d1_mini) | There's also a [Pro Version](https://www.aliexpress.com/store/product/WEMOS-D1-mini-Pro-16M-bytes-external-antenna-connector-ESP8266-WIFI-Internet-of-Things-development-board/1331105_32724692514.html) with 16MB of flash memory instead of 4MB. Only buy from [LoLin](https://lolin.aliexpress.com/store/1331105) on Aliexpress, there are many counterfeits of varying quality |
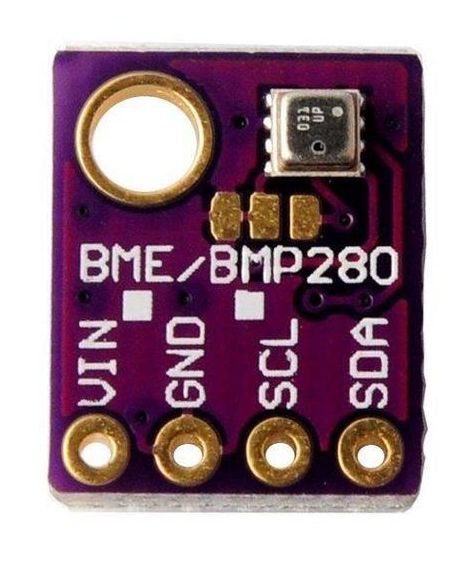
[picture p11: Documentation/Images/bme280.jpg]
|  | BME280 Temp Humidity Pressure Sensor | 1 | $2.50 | [AliExpress](https://www.aliexpress.com/item/3In1-BME280-GY-BME280-Digital-Sensor-SPI-I2C-Humidity-Temperature-and-Barometric-Pressure-Sensor-Module-1/32831977783.html) | [Datasheet](https://ae-bst.resource.bosch.com/media/_tech/media/datasheets/BST-BME280_DS001-11.pdf) | Make sure to get the square sensor and square board, not the BMP280 (that lacks humidity) |
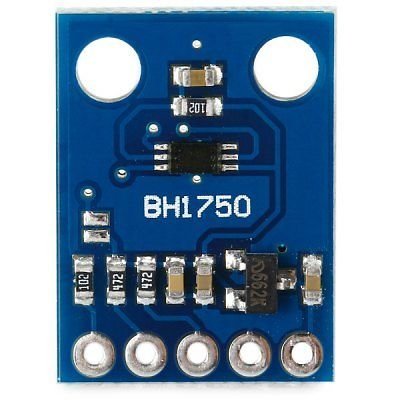
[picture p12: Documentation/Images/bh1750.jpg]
|  | BH1750FVI Digital Light Sensor | 1 | $1.10 | [AliExpress](https://www.aliexpress.com/item/GY-302-BH1750-Chip-Light-Intensity-Light-Module-Freeshipping-Dropshipping/1766481544.html) | [Datasheet](http://rohmfs.rohm.com/en/products/databook/datasheet/ic/sensor/light/bh1750fvi-e.pdf) |  |
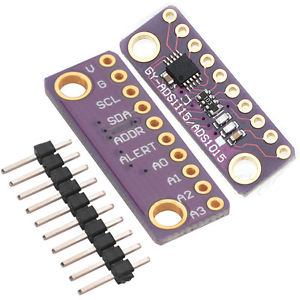
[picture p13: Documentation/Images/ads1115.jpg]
|  | ADS1115 16bit Analog to Digital Converter | 1 | $2.00 | [AliExpress](https://www.aliexpress.com/item/I2C-ADS1115-16-Bit-ADC-4-channel-Module-with-Programmable-Gain-Amplifier-2-0V-to-5/32826605867.html) | [Datasheet](http://www.ti.com/lit/ds/symlink/ads1115.pdf) | There are several pinout configurations/colors available that are incompatible with each other. Our design needs the pins in the following order: VCC (V), Gnd (G), SCL, SDA |
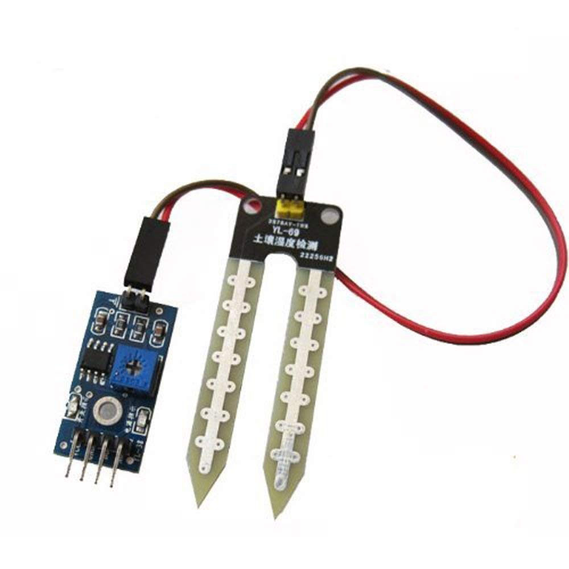
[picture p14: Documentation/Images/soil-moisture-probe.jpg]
|  | Generic Soil Moisture Sensor | 1 | $0.40 | [AliExpress](https://www.aliexpress.com/item/1PCS-Smart-Electronics-Soil-Hygrometer-Humidity-Detection-Module-Moisture-Water-Sensor-Soil-moisture-for-Arduino/32860007226.html) | N/A | There are various options. We used [gold-plated probes](https://www.aliexpress.com/item/86062-Soil-Hygrometer-Humidity-Detection-Module-Moisture-Water-Sensor-Soil-moisture-for-Arduino/32705056123.html), but we now prefer the 2-wire probes with silver solder and a separate module (see photo). Gold plated probes suffer more corrosion. Calibration coefficients are available for both types in our Calibration analysis. |
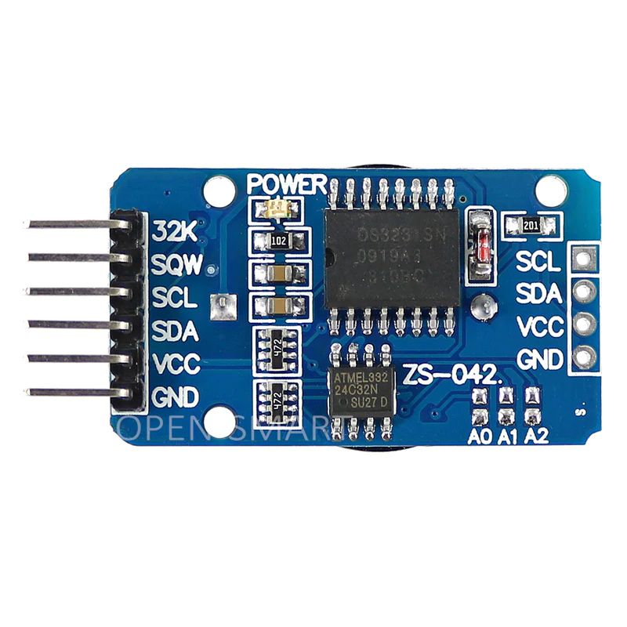
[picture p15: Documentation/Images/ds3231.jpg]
|  | DS3231SN Real Time Clock | 1 | $1.15 | [AliExpress](https://www.aliexpress.com/item/DS3231-AT24C32-IIC-Module-Precision-Clock-Module-DS3231SN-for-Arduino-Memory-module-Free-Shipping/1767001372.html) | [Datasheet](https://datasheets.maximintegrated.com/en/ds/DS3231.pdf) | Get the SN version (rated to -40C), not the N version (0C). There is also an M version, that is rated to -40C and more resistant to vibration, but slightly less accurate. Even if you order the SN version, they're often a mix of all three versions, so it's wise to order extra. |
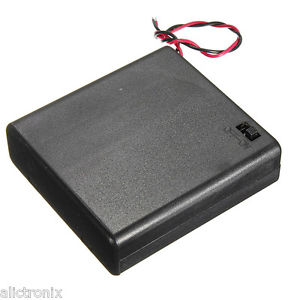
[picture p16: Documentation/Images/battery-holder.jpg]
|  | 4xAA Battery Holder w/Switch | 1 | $1.14 | [AliExpress](https://www.aliexpress.com/item/1PCS-ON-OFF-Switch-Plastic-Cover-4x-1-5V-AA-Batteries-Case-Box-Holder-With-Wires/32681663145.html) | N/A | Buy extra, these sometimes have defects. Some can be fixed via soldering inside. |
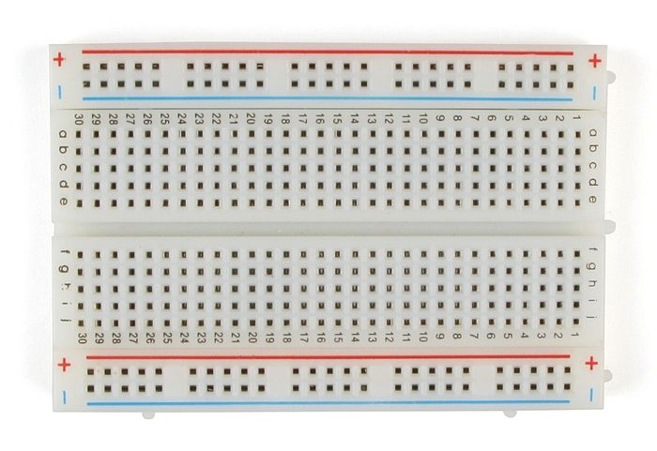
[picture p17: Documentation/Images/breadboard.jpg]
|  | 400 Tiepoint Breadboard | 1 | $1.20 | [AliExpress](https://www.aliexpress.com/item/PCB-Test-Mini-Breadboard-Bread-Board-400-Contacts-Available-8-5-x-5-5cm-New-8/32614008350.html) | N/A | Get ones with rounded (not angular) side tabs. They seem to be higher quality. |
|  | NDP6020P P-Channel MOSFET (10 pcs) | 1 | $1.16 | [Sample](https://www.fairchildsemi.com/products/discretes/fets/mosfets/NDP6020P.html) [AliExpress](https://www.aliexpress.com/item/10pcs-lot-NDP6020P-NDP6020-MOSFET-P-CH-20V-24A-TO-220/32891876960.html) | [Datasheet](https://www.fairchildsemi.com/datasheets/ND/NDP6020P.pdf) | This acts as a power switch with the DS3231 clock. Enough for 10 EMUs |
| | 100k Ω Resistors (100pcs) | 1 | $0.63 | [AliExpress](https://www.aliexpress.com/item/100pcs-1-4W-1R-22M-1-Metal-film-resistor-100R-220R-1K-1-5K-2-2K/32847096736.html) | | any 1/4W should be fine. 100pcs is enough for 50 EMUs |
| | 330k Ω Resistors (100pcs) | 1 | $0.63 | [AliExpress](https://www.aliexpress.com/item/100pcs-1-4W-1R-22M-1-Metal-film-resistor-100R-220R-1K-1-5K-2-2K/32847096736.html) | | 1/4W 1% tolerance. 100pcs is enough for 100 EMUs |
|  | 140-pc kit U-shaped jumper wire kit | 1 | $2.00 | [AliExpress](https://www.aliexpress.com/item/Free-Shipping-140pcs-in-one-package-convenient-New-Solderless-Flexible-Breadboard-Jumper-wires-Cables-HOT-Sale/1347939034.html) | N/A | 1 kit should be enough for 2-4 EMUs |
|  | Dupont Female Connector kit | 1 | $2.88 | [AliExpress](https://www.aliexpress.com/item/150PCS-2-54mm-Plastic-Dupont-Jumper-Wire-Kit-With-Box-1P-2P-3P-4P-5P-6P/32722201898.html) | N/A | Not required but really helps reliability/organization. One kit is enough for ~10 EMUs |
|  | AA Batteries | 4 | $2-5 | N/A | N/A | Name brand preferred (e.g., Duracell, Energizer). Applications in extreme temperatures may require Lithium AA batteries (wider operating temperature range) |
|  | CR2032 Coin Cell Battery (10 pcs) | 1 | $1.70 | [AliExpress](https://www.aliexpress.com/item/Cheap-Free-Shipping-10pcs-CR2032-BR2032-DL2032-SB-T15-EA2032C-ECR2032-L2032-CR-2032-Lithium/32778320423.html) | N/A | For DS3231 clocks (1/EMU). Chinese batteries are usually fine, but for high reliability or long durations, go with US name brands. |
|  | MG Chemicals Silicone Modified Conformal Coating | 1 | $12.95 | [Amazon](https://www.amazon.com/MG-Chemicals-Silicone-Conformal-Coating/dp/B004SPJOKK) | [MSDS](https://www.mgchemicals.com/downloads/msds/01%20English%20Can-USA%20SDS/sds-422b-l.pdf) | 55 mL is enough for 50+ EMUs. Paint onto sensors and circuit boards, especially the external ones. |
|  | Nanoprotech Electrical Anti-corrosion Spray | 1 | $20.00 | [Amazon](https://www.amazon.com/Nanoprotech-Multi-use-Protective-Automotive-Electrical/dp/B00RZUZVC0) | N/A | 1 can is enough for at least 50-100 EMUs. Spray or paint onto external electrical connections. |
|  | 0.8mm 63/37 Solder Wire | 1 | $ | [AliExpress](https://www.aliexpress.com/item/High-Quality-63-37-Rosin-Core-Welding-Flux-2-Tin-Lead-Solder-Iron-Wire-Reel-0/32774426766.html) | N/A | A 100g role is enough for ~20-40 EMUs 
|  | 10cm 40-pin F-M Dupont Cable | 1 | $0.60 | [AliExpress](https://www.aliexpress.com/item/WAVGAT-40pcs-10cm-2-54mm-1pin-1p-1p-male-to-female-jumper-wire-Dupont-cable-for/32825839970.html) | N/A | We use these to connect the soil moisture sensor module to the breadboard. One cable is enough for 12 EMUs (3 random-colored wires/EMU) or 4 EMUs (color-coded) |
|  | 30cm 40-pin F-M Dupont Cable | 1 | $1.10 | [AliExpress](https://www.aliexpress.com/store/product/Dupont-Line-40pcs-30cm-Female-to-Male-Jumper-Wire-Dupont-Cable/3241083_32839425460.html) | N/A | We use these to attach the BH1750 and BME280 sensors using color-coded wires. One cable is enough for 4 EMUs (8 wire colors/EMU) |
|  | 30cm 40-pin F-F Dupont Cable | 1 | $0.85 | [AliExpress](https://www.aliexpress.com/item/Dupont-Line-40pcs-30cm-Female-to-Female-Jumper-Wire-Dupont-Cable/32841975022.html) | N/A | We use these to attach soil moisture probes to the module. One cable is enough for 20 EMUs (2 wires/EMU) |
|  | ~900 mL gasketed container | 1 | $2-4 | N/A | N/A | Any grocery store has a variety of these. We get ours from Ocean State Job Lot for $2. It's easier to drill holes in the slightly flexible polypropylene, rather than brittle acrylic. |

## Testing Equipment & Other Useful Parts

| &nbsp;&nbsp;&nbsp;&nbsp;&nbsp;&nbsp;&nbsp;&nbsp;&nbsp;&nbsp;&nbsp;Photo&nbsp;&nbsp;&nbsp;&nbsp;&nbsp;&nbsp;&nbsp;&nbsp;&nbsp;&nbsp;&nbsp; | &nbsp;&nbsp;&nbsp;&nbsp;&nbsp;&nbsp;&nbsp;&nbsp;&nbsp;&nbsp;&nbsp;&nbsp;Part&nbsp;&nbsp;&nbsp;&nbsp;&nbsp;&nbsp;&nbsp;&nbsp;&nbsp;&nbsp;&nbsp;&nbsp;&nbsp; | Number | Cost | Source | Datasheet | Notes |
| :---: | :--- | :---: | :---: | :---: | :---: | :--- | 
|  | Yihua 947-III 60W adjustable soldering iron (with 900-M tips) | 1 | $10.00 | [AliExpress](https://www.aliexpress.com/item/110V-220V-Optional-Welding-Soldering-Iron-60W-YIHUA-947-III-Set-For-Soldering-Kit-With-Temperature/32785900623.html) | N/A | We like these soldering irons. A clone of the Hakko 900-M, uses the same tips. |
|  | Soldering Iron Stand | 1 | $1.99 | [AliExpress](https://www.aliexpress.com/item/Metal-Iron-Useful-Solid-Metal-Base-Soldering-Iron-Bracket-Stand-Holder-Support-Station-Frame-Portable-for/32852907489.html) | N/A |  |
|  | Soldering Iron Tip Cleaner | 1 | $2.75 | [AliExpress](https://www.aliexpress.com/item/1pcs-Wire-With-Stand-Set-Welding-Soldering-Solder-Iron-Tip-Cleaner-Cleaning-Steel-Hot-Selling/32889857477.html) | N/A |  |
|  | Victor 81D Autoranging Multimeter | 1 | $18.29 | [AliExpress](https://www.aliexpress.com/item/81D-Victor-RuoShui-Digital-Multimeter-4000-Counsts-Auto-Range-True-RMS-Resistance-Capacitance-Frequency-Temperature-Multimetro/32910618248.html) | [Manual](https://www.electrokit.com/uploads/productfile/41004/VICTOR81D.pdf) | They're cheap, but have good features. |
|  | Jakemy CT4-12 wire strippers | 1 | $5.00 | [AliExpress](https://www.aliexpress.com/item/AWG22-10-7-Wire-Stripper-Pliers-Decrustation-Pliers-Cable-Wire-Stripping-Pliers-Herramientas-Hand-Tools/32758418451.html) | N/A | These are well-made and excellent! |
|  | Voxlink Micro USB Cords | 1-5 | $2.00 | [AliExpress](https://www.aliexpress.com/item/VOXLINK-5Pack-Micro-USB-Cable-Fast-Charging-Microusb-Data-Cable-for-Samsung-S6-S7-S5-S4/32876384106.html) | N/A | We have good results with Voxlink or Anker brands |
|  | 128x64 I2C OLED Display (SSD1306) | 2 | $2.00 | [AliExpress](https://www.aliexpress.com/item/White-Blue-White-and-Blue-color-0-96-inch-128X64-OLED-Display-Module-For-arduino-0/32767499263.html) | [Datasheet](https://cdn-shop.adafruit.com/datasheets/SSD1306.pdf) | Useful display, can be used with the NodeMCU u8g2 hardware module |
|  | CP2102 Micro USB to Serial Module | 1 | $1.00 | [AliExpress](https://www.aliexpress.com/item/CJMCU-CP2102-USB-To-TTL-Serial-Module-UART-STC-Downloader-For-Arduino/32478532097.html) | N/A | These let you interface an EMU without supplying power via the built-in USB port. Useful for debugging. They also support up to 921600 baud (higher file transfer rates). You need to install the [driver](https://www.silabs.com/products/development-tools/software/usb-to-uart-bridge-vcp-drivers) to use them. Connect TX to RX, RX to TX, and GND to GND |
|  | A small set of various standard resistor values | 1 | $2.15 | [AliExpress](https://www.aliexpress.com/item/Best-Promotion-1-1-4W-Metal-Film-Resistor-Assortment-Kit-Set-20-Kinds-Value-Total-400pcs/32662401735.html) | []() | especially 1k, 2.2k, 4.7k, 10k, 47k and 100k. 1/4W 1% or 5% are good |
|  | Heat shrink tubing kit | 1 | $2.69 | [AliExpress](https://www.aliexpress.com/item/328Pcs-Assorted-Heat-Shrink-Tubing-Car-Electrical-Cable-Tube-kits-Wrap-Sleeve-8-Sizes-Mixed-Color/32789316380.html) | N/A | Assorted sizes. We use this for things like pins soldered to the battery pack wires |
|  | 2.54mm pin headers, 40-pin male | 1 | 0.57 | [AliExpress](https://www.aliexpress.com/item/10pcs-40-Pin-1x40-Single-Row-Male-2-54-Breakable-Pin-Header-Connector-Strip-for-Arduino/32864438850.html) | N/A | These are useful to have around as replacements or fixes for bad soldering. We also use them to solder battery wires to. There are several sizes, male and female, and straight and bent. Straight male are the most useful. |

## Other Resources

[Edward Mallon](https://edwardmallon.wordpress.com/) (a fantastic resource!) has a similar parts/tools list for [his logger](https://edwardmallon.wordpress.com/2016/10/27/diy-arduino-promini-data-logger-2016-build-update/) and [classroom kits](https://edwardmallon.wordpress.com/2016/08/08/build-your-own-arduino-classroom/). Useful for comparison and additional parts/tools.

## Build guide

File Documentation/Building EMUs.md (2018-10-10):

# Building EMUs

With the [appropriate parts](Parts%20list.md), you can build your own EMUs. Our [video](https://www.youtube.com/watch?v=74yjZC-QKPY) associated with the paper steps through this process, below is some additional information.

## Soldering

Proper soldering takes some training or experience, and we recommend that those new to soldering educate themselves, especially on safety. Here is a [video beginner tutorial](https://www.youtube.com/watch?v=Qps9woUGkvI), and a series of [9 video lessons](https://www.youtube.com/playlist?list=PL926EC0F1F93C1837)(1 and 6 are especially relevant). At a minimum, we recommend safety goggles, good ventilation, a soldering iron tip cleaner, a clear workspace that keeps the cord away from the iron, and a sturdy soldering iron stand.

Sensors and the D1 Mini generally come without the pins soldered into the circuit board. Some (e.g. the D1 Mini) come with more than one pin type. We solder these on, using the long female pin headers for the D1 Mini. One could solder wires directly to the sensors, rather than these pins, however, we prefer the pins because it allows for easy sensor replacement.

Additionally, we make several small modifications to the pre-build sensor modules (see [video](https://www.youtube.com/watch?v=74yjZC-QKPY), [paper supplement]()):

1. Since the BME280, BH1750, ADS1115 and DS3231 all share the same I2C wires, the pullup resistors on the SCL and SDA lines present on all four modules are redundant, wasting some electricity. We remove those on the BH1750 (marked 472), and the DS3231 clock (4x472 block across from the VCC pin).
2. Removing the 4x472 block on the DS3231 clock also removes the pullup resistor on the SQW pin. Failure to remove this resistor prevents the clock SQW alarm pin from turning on the MOSFET switch.
3. We remove the resistor marked 102 on the DS3231SN clock (near SCL of the 4-pin header side). This resistor is for charging rechargeable LR2032 batteries, but we prefer to use non-rechargeable CR2032 batteries that are cheaper and last for years, and a charge current can degrade these batteries. See [Ed Mallon](https://thecavepearlproject.org/2014/05/21/using-a-cheap-3-ds3231-rtc-at24c32-eeprom-from-ebay/) and [Beddows & Mallon 2018](https://doi.org/10.3390/s18020530).

## Breadboard Wiring Connections

Breadboards rows numbered from 1-30 and columns lettered from A to J. Within a row, holes A-F are connected to each other, and G-J are connected. Additionally, breadboards have 2 columns labeled (+) and (-) on each outer side. These columns or "rails" are usually used to distribute power. In our setup, the left rails (beside column A) are used for battery power. The right (+) rail (beside column J) is used for 3.3v power (from the D1 Mini), and the right (-) rail is unused.

Breadboard

To wire an EMU breadboard, plug in the wires denoted below, roughly in the order they appear using their row and column addresses, then the components. Generally, we use longer 10-30 cm wires to connect the BME280, BH1750, and soil moisture module to the breadboard, rather than plugging them in directly, but this can be specific to application.

| **Component** | **Start** | **End** | **Function** | **Notes** |
| :---: | :---: | :---: | :---: | :---: |
| Wire | (-) | A2 | Grounding for D1 Mini |  |
| Wire | (-) | A11 | Grounding for D1 Mini | For redundancy |
| Wire | (+) | A13 | Power to the MOSFET | Battery voltage |
| Wire | (-) | A22 | Grounding for clock, BME280, ADS1115, &amp; BH1750 |  |
| Wire | (-) | A29 | Grounding for soil moisture probe |  |
| Wire | B21 | B28 | Power for soil moisture probe | 3.3v |
| Wire | B19 | F23 | Clock I2C - SCL line |  |
| Wire | B20 | F24 | Clock I2C - SDA line |  |
| Wire | C2 | C11 | Grounding for D1 Mini | For redundancy |
| Wire | E5 | E22 | Sensors &amp; Clock I2C - SCL line |  |
| Wire | E6 | E24 | Sensors &amp; Clock I2C - SDA line |  |
| Wire | E10 | E14 | Power from the MOSFET to the D1 Mini | Battery voltage |
| Wire | E15 | E18 | Clock alarm to the MOSFET | Turns power on |
| Wire | E21 | F21 | Power for soil moisture probe and clock | 3.3v |
| Wire | E22 | F22 | Grounding for BME280, ADS1115, &amp; BH1750 |  |
| Wire | E30 | F27 | Soil moisture probe signal to ADS1115 |  |
| Wire | F8 | H6 | Enables waking from sleep for D1 Mini | Clock failsafe |
| Wire | J1 | (+) | Power to the right breadboard rail | 3.3v; all sensors & clock|
| Wire | J21 | (+) | Power to sensors &amp; clock | 3.3v |
| 330k ohm Resistor | C1 | F7 | Measures battery voltage | Either orientation |
| Wire | D1 | D10 | Power from the MOSFET to the D1 Mini | Battery voltage |
| 100k ohm Resistor | D13 | D15 | Pullup for MOSFET | Either orientation |
| 100k ohm Resistor | J5 | (+) | Pullup for code disable pin | Either orientation |
| NDP6020P P-MOSFET 3-pin | C13 | C15 | Power switch | Orientation matters: Source→C13, Drain→C14, Gate→C15 |
| Lolin D1 Mini Microcontroller | B1/H1 | B8/H8 | The brains of the EMU | B1→5V, I1→3.3V |
| DS3231SN Module | D17 | D22 | Clock: timekeeping & power management | GND→D22, VCC→D21, SDA→D20, SCL→D19, SQW→D18|
| ADS1115 Module | I21 | I30 | Analog to digital converter for soil moisture | align VCC→I21 |
| Soil Moisture Sensor Module | D28 | D30 | Soil moisture sensor | VCC→D28, GND→D29, AO→D30 |
| BME280 Module | H21 | H24 | Temp/humidity sensor | VCC→H21, GND→H22, SCL→H23, SDA→H24 |
| BH1750FVI Module | G21 | G24 | Light sensor | VCC→G21, GND→G22, SCL→G23, SDA→G24 |
| 4xAA Battery Pack | (+) | (-) | Battery power | Hook up (+) and (-) to the side adjacent to row A |

## Waterproofing

We recommend coating the circuit boards of the BME280 and BH1750 with [MG Chemicals silicone modified conformal coating](https://www.mgchemicals.com/products/conformal-coatings/silicone-conformal-coating-422b) after soldering pins on. Be very careful not to cover the light sensor (black rectangle) on the BH1750 module or the humidity sensor hole (tiny hole in silver square) on the BME280 sensor. Coating internal components (especially higher value modules such as the D1 Mini) is a good idea as well.  In the event of water leakage, these can be salvaged and reused. In our testing, this coating has the best weatherproofing capability. It can be painted on, removed with acetone, and coatings can be quality-checked using a UV light.

External wiring connections or pins cannot be coated with silicone conformal coating: this would prevent the connection.  Therefore, for these we use [Nano Protech nano-partical anti-corrosion spray](http://nanoprotech.org/).  This spray works relatively well, but may need to be reapplied over long periods.  We recommend keeping external wiring connections to the bare minimum. We experimented with shrink-wrap tubing to coat wiring connections, but instead these trapped water, making the problems worse.

## Temperature Sensor Shielding

Temperature sensors should be shielded from the sun, and perhaps also from the ground to prevent elevated temperature reading. Ideally, shielding should be [fan-aspirated](https://www.apogeeinstruments.com/aspirated-radiation-shield/), to prevent air from being trapped near the sensor. Alternatively, naturally aspirated [gill shields](https://www.onsetcomp.com/products/mounting/rs3-b), provide accuracy to within 1-2 °C when there is no wind to create air movement (and higher accuracy in other conditions). Unfortunately, both of these options are prohibitively expensive relative to EMUs.

Instead of buying a shield, we built one out of an inverted white plastic cup bottom, similar to [Cowles et al. 2016](https://doi.org/10.1111/gcb.13111). Subsequently, [Terando et al. 2017](http://doi.org/10.1002/ece3.3499) have done careful tests and concluded that this is not a good design and can even be worse than no shielding in some circumstances.  Instead, they recommend one built by [Holden et al. 2013](https://doi.org/10.1016/j.agrformet.2013.06.011) ([video instructions for construction](https://www.youtube.com/watch?v=LkVmJRsw5vs)) out of corrugated plastic material covered with foil tape. This shield provides similar shielding to naturally-aspirated gill shields. 

Regardless of the shielding used, we recommend that researchers carefully consider their shielding design, and if it has not already been tested against a high quality shield and temperature sensor, we recommend that this be done.

## Lessons Learned from Novice Builders

*In General*:
- Orientation of sensors and pins should ALWAYS be checked before anything is added or 
removed.
- Each sensor or module should be tested separately to ensure it’s working properly before final assembly. 
- Safety precautions should be thoroughly examined before each process.

*Soldering*: 
- For anyone’s first time soldering it’s important to note how to properly hold the solder and soldering iron as well as to understand ventilation and safety concerns.  
- Good ventilation (at least a fan) should be used while soldering. Safety glasses and aprons are advised. 
- Looking up instructional videos explaining how to solder properly is advised for beginners. (Please see [Soldering](Building%20EMUs.md#soldering) for more information/videos on soldering)
- The type of soldering tip is important.  For removing resistors, a larger flatter tip was found to be easier rather than the common pencil type tip used for soldering pins. 
- Always turn off the soldering iron when not in use. 
- Orientation of pins should be triple checked before soldering.
- Be safe!

*Wiring*: 
- Using pre-cut wires saves time, though it is not required.
- It is better to take your time when wiring the breadboard. After all of the components are added, it makes it more difficult to recheck the positioning of the wires. 

*Waterproofing*: 
- Make sure that when painting the sensors with the silicone conformal coating, the actual sensor portion of the components are not covered. For example, the area on the light sensor that actually does the sensing should not be covered.  Shining UV light shows whether any coating has covered this area. 
- Fume hoods and ventilation should be used when using waterproofing coatings or sprays. 
- Heat shrink tubing should be pre cut and pay attention to the size used.  Looking up instructional videos on how to properly and safely use a heat gun is advised. Alternatively, any flame source is sufficient, but safety still applies.

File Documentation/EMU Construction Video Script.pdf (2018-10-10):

## EMU Construction Video Script

The following is the script for our EMU construction video below: https://youtu.be/74yjZC-QKPY

Video Visuals | Audio & Captions
Title: EMU Construction Video “Part I: Parts Overview” -Components of EMU are shown and described | Right now we are going to show you the main components of these ecological sensor units. First, we have the breadboard which we will cover in detail later on. Next we have WeMos D1 mini, with the wifi chip on the top here and usb connector in the front of the unit. Next we have the P-channel MOSFET switch. And this is the DS3231 clock which as you can see requires its own watch battery for our set up. Here we have the ADS1115 16 bit Analog to Digital Converter which is used in conjunction with the soil moisture probe. Moving on to the sensors: We have the BME 280 temperature, humidity and air pressure sensor. This is the BH1750 light sensor, and this is the soil moisture sensor. The batteries for the unit are housed in this battery case. Here we have a case that can hold 3 standard AA batteries. *Note: We switched to 4xAA batteries for better performance. For a full parts list please take a look at the links below.

“Part II: Soldering the Sensors”

-Resistors are removed off of clock and BH1750

Of course, not everything comes ready to assemble, so in this part we will have to alter some of the sensors.
If you never soldered before don’t worry! I’d advise practicing a few times before this next step.

Using your solder, we want to carefully remove 2 resistors from the clock. The first one we are removing is the resistor next to SDA and VCC on the right side of the sensor that has a small label saying “472”. To remove, heat up your soldering tool and delicately push from the side of the resistor until it comes loose. Use the same process now with the second resistor that says “102” in the top left corner of the sensor.

*Note: Removing the 472 resistor from the clock removes the pullup on the SQW pin. This is required to use the clock to turn on the MOSFET in our setup. Additionally, removing this resistor gets rid of the pullups on the SCL and SDA I²C data lines. When other I²C sensors are included (as in our setup) these are redundant.

*Note: Removing the 102 resistor disables charging of the internal battery. This does not work well anyway at 3.3v, and we prefer the non-rechargeable CR2032 battery, which can be damaged by charging.

Next you are going to remove the two 472 resistors from the top of the top of the BH1750 light sensor.

*Note: As with the clock above, these resistors are for the I²C data lines and are redundant if more than one I²C sensor is used.

“Part III: Wiring the Breadboard”

-Step by step instructions of wiring the breadboard are described

If you have never dealt with a breadboard it’s okay! Think of a breadboard as an electrical circuit. The + and – are “power rails” which is where you can easily get power from in your breadboard. The “horizontal rows” in the middle area are also separately connected from columns A through E and then columns F through I, and then again we have “power rails” columns + and - again on the other side. It is important to remember that the 2 power rails are separate, they are not connected.

To start, let’s begin on the uppermost corner of the breadboard. You want to cut a wire that will connect from (-) to A2.

As a side note, it doesn’t matter where in the (-) or (+) the wires are being placed into, the spots in each row have the same positive or negative charge.

Next, cut a similar length wire to attach (-) to A11.

Moving down the breadboard, next up is connecting (+) to A13.

Link column (–) to A22 and then (-) to A29.

Moving over into column B, cut a wire a bit longer to join the following wires from:
B21 to B28
B19 to F23
B20 to F24

Now move along to column C. You are going to take a wire, even longer than the last wire you cut, and connect C2 to C11.

Moving over to column D, join D1 to D10.

*Note: the D1-D10 wire is actually redundant with C2-C11. The ESP8266 is very sensitive to grounding, and we find that two wires sometimes improves reliability

Column E is where the wiring gets a bit tricky. Using a long piece of wire attach it from E5 to J23 and then another from E6 to J24.

Then use a small piece of wire for E10 to E14 and E15 to E18.

Continuing down the breadboard, you are going to cut 2 small pieces of wires for the following:
E21 to F21
E22 to F22
And use a slightly longer wire for E30 to F27.

Now on the other side of the breadboard, use 3 small pieces of wire to attach:
J1 to (+)
J21 to (+)
F8 to H6

Hang in there guys! Only a couple more steps until Part 4.

Next add the resistors. 2 types of resistors are needed: 330k and 100k. The 100k resistor connects 13 to 15 in column D and the 330k joins column C1 to H7 and another in J5 to (+). Be careful to make sure the wires from the resistors are not touching the exposed segments of the connectors.

* Note: The resistor from D13-D15 is a “pullup resistor” that pulls the MOSFET gate weakly to (+) to make sure it is “off”. When we give it (-) from the clock, it turns on the switch.

*Note: The 330k resistor allows the D1 Mini to measure battery voltage up to 6.5v. Without it, the D1 Mini can only measure voltage up to 3.3v

*Note: J5 to (+) is actually 100K resistor, another pullup used to disable code from running.

Lastly, grab the p-channel MOSFET 3 pin and place them in the left side of the breadboard from C13 to C15.

* Note: The MOSFET must be oriented in same direction as in the video.

“Part IV: Final Assembly”

-All components are attached and unit is shown in environment.

Next up on our list is to install the Wemos, ADS1115, DS3231 clock, BH1750 sensors, and the wires for the BME280, BH1750, and soil moisture probes which will be the only sensors located on the outside of the container. In order to install the wemos sensor, you are going to line up the 5V pin on the Wemos into B1 and the 3V3 pin into I1.

Next, take the ADS1115 and attach the ground pin to I21 to I30. The DS3231 clock is placed from D17 to D22.

The wires for the BH1750 light sensor attaches to G21 to G24.

*Note: Make sure the order of the sensor pins matches ADS1115 on breadboard

The wires for the BME280 attaches to H21 to H24. Lastly, the wires for the soil moisture probe attach to D28 to D30.

Finally, the battery pack can be connected to the breadboard by placing the plus and minus wires the corresponding positive and negative columns on the top of the breadboard. *Note: Make sure to attach battery to +/-strip next to column A, rather than column J.
Now that we have everything wired to the breadboard, we can seal the container. Now we are ready to see it in action

The EMU unit is not only capable of being made at home, but it is also accurate and cost effective compared to other sensors currently on the market. To learn more about the setup, parts, or see our comparative data results please look at the attached links in the description below.
https://github.com/mickley/EMU

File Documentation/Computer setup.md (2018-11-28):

# Setting Up Your Computer to Work with EMUs

Programming the ESP8266 is done using [Esplorer](http://esp8266.ru/esplorer-latest/?f=ESPlorer.zip) or [NodeMCU-uploader](https://github.com/kmpm/nodemcu-uploader).  Both work on Windows and OSX.  Esplorer requires [Java](https://www.java.com/en/download/help/download_options.xml) to be installed, and NodeMCU-uploader requires [Python](https://www.python.org/downloads/).

In order to use EMUs with your computer, there are several software aspects to install
1. **Drivers:** The Lolin D1 Mini uses the CH340G USB to serial chipset. In order to connect, you need to install the driver for this
2. **Firmware Flasher:** You need a program to flash a firmware to the D1 Mini: either [nodemcu-pyflasher](https://github.com/marcelstoer/nodemcu-pyflasher) or [esptool](https://github.com/espressif/esptool)
3. **Programming IDE:** You need a program to run code, display output, and download data from the D1 Mini, [ESPlorer](https://esp8266.ru/esplorer/) is the best option and works on Windows, OSX, and Linux
4. **(optional) Commandline Interface:** [nodemcu-uploader](https://github.com/kmpm/nodemcu-uploader) allows you to run, upload, and download files via the commandline. Note that it requires [Python](https://www.python.org/downloads/) and pip (installs with latest Python) to be installed.

## Windows

1. Download and unzip the [Windows CH340G driver](/Drivers/CH340G%20-%20Windows%20-%20v3.4.2014.8.zip). Run Setup.exe and click the Install button. If a prompt appears about an unsigned Windows driver, allow it. A step-by-step guide is [here](http://www.dnatechindia.com/ch340g-drivers-download-installation-guide.html). If the driver is installed correctly, plugging in a D1 mini should result in a device showing up in Devices and Printers with the associated COM port name (e.g., COM7). This is the port you use to connect with.
2. Download [nodemcu-pyflasher](https://github.com/marcelstoer/nodemcu-pyflasher/releases)
Install the Windows CH340G driver.
3. Download [ESPlorer](http://esp8266.ru/esplorer-latest/?f=ESPlorer.zip), and set up (see below). Generally, if java is set up correctly, you can run it by clicking on the ESPlorer.jar or ESPlorer.bat files. Alternatively, in a command prompt, switch to the ESPlorer folder and run `java -jar ESPlorer.jar`. ESPlorer requires [Java SE version 7 or 8](https://www.java.com/en/download/manual.jsp). You may have problems running it with Java version 9 and may need to roll java back. 

## Mac OSX

1. CH340G driver installation for OSX sometimes has problems, and there are now several versions of the driver circulating. We have had good results with [this one that we include here](/Drivers/CH340G%20-%20Mac.zip), but [this website](https://kig.re/2014/12/31/how-to-use-arduino-nano-mini-pro-with-CH340G-on-mac-osx-yosemite.html) maintains a resource dedicated to getting the working for various versions of OSX. You will likely need to go to System Preferences > Security and Privacy and allow apps downloaded from Anywhere to be run. If the driver is installed correctly, plugging in a D1 Mini and running `ls /dev/cu*` from a terminal should list a serial port name starting with `cu.wchusbserial`. This is the port you use to connect with.  If the driver does not work, there is an uninstallation procedure [here](https://sparks.gogo.co.nz/ch340.html).
2. Download [nodemcu-pyflasher](https://github.com/marcelstoer/nodemcu-pyflasher/releases)
3. Download [ESPlorer](http://esp8266.ru/esplorer-latest/?f=ESPlorer.zip), and set up (see below). Generally, if java is set up correctly, you can run it by clicking on the ESPlorer.jar file. Alternatively, in a terminal, switch to the ESPlorer folder and run `java -jar ESPlorer.jar`. ESPlorer requires [Java SE version 7 or 8](https://www.java.com/en/download/manual.jsp). You may have problems running it with Java version 9 and may need to roll java back. 

## Linux

The support for working with EMUs in Linux is not as good as with Windows and OSX and is less well-tested.  We recommend that only experienced Linux users attempt this.  Help on the internet may be difficult to find.

1. In many versions of Linux, no driver installation is required. If that is not the case, there is a Linux driver available [here](https://sparks.gogo.co.nz/ch340.html). If the driver is installed correctly, plugging in a D1 Mini and running `ls /dev/ttyUSB` from a terminal should list a serial port name such as `ttyUSB0`. This is the port you use to connect with. You will also need to have user permissions to access the /dev/ttyUSB0 device. On Linux, you can enable this by adding your user to the dialout group with `sudo adduser <username> dialout`, and rebooting or logging out and in again. Without fixing the permissions issue, ESPlorer will be unable to access the serial port.
2. Install [esptool](https://github.com/espressif/esptool).  Note: this requires [Python](https://www.python.org/downloads/) and pip (installs with latest Python) to be installed.  Often, this is already the case, however.  Alternatively, it should be possible to build [nodemcu-pyflasher](https://github.com/marcelstoer/nodemcu-pyflasher) from source for Linux, though no release currently provided.
3. Download [ESPlorer](http://esp8266.ru/esplorer-latest/?f=ESPlorer.zip), and set up (see below). Generally, if java is set up correctly, you can run it by clicking on the ESPlorer.jar file. Alternatively, in a terminal, switch to the ESPlorer folder and run `java -jar ESPlorer.jar`. ESPlorer requires [Java SE version 7 or 8](https://www.java.com/en/download/manual.jsp). You may have problems running it with Java version 9 and may need to roll java back. 

## Setting up ESPlorer

Open ESPlorer, and click on the Settings tab, where we'll make some changes (Example screenshot below):

* Uncheck AutoSave file to disk before save to ESP
* Uncheck AutoSave file to ESP after save to disk
* Uncheck Autodetect firmware
* Uncheck Command Echo
* Check "Turbo Mode"
* Set Delay after answer to 0 ms
* If there is an option to, uncheck AutoRun file after save to ESP
* At the top, beside the large Open button is a dropdown that is set at 9600 by default.  This is the baud or connection speed.  Set this to 115200, which is the speed that the EMU communicates with by default.
* Click on the Snippets Tab.  Click Edit Snippet0.  Name it Abort, and put abort=1 in the box and click Save

There's also a tutorial for using Esplorer [here](http://www.engineersgarage.com/tutorials/getting-started-esplorer-ide). and an ebook on it [here](http://esp8266.ru/download/esp8266-doc/Getting%20Started%20with%20the%20ESPlorer%20IDE%20-%20Rui%20Santos.pdf).

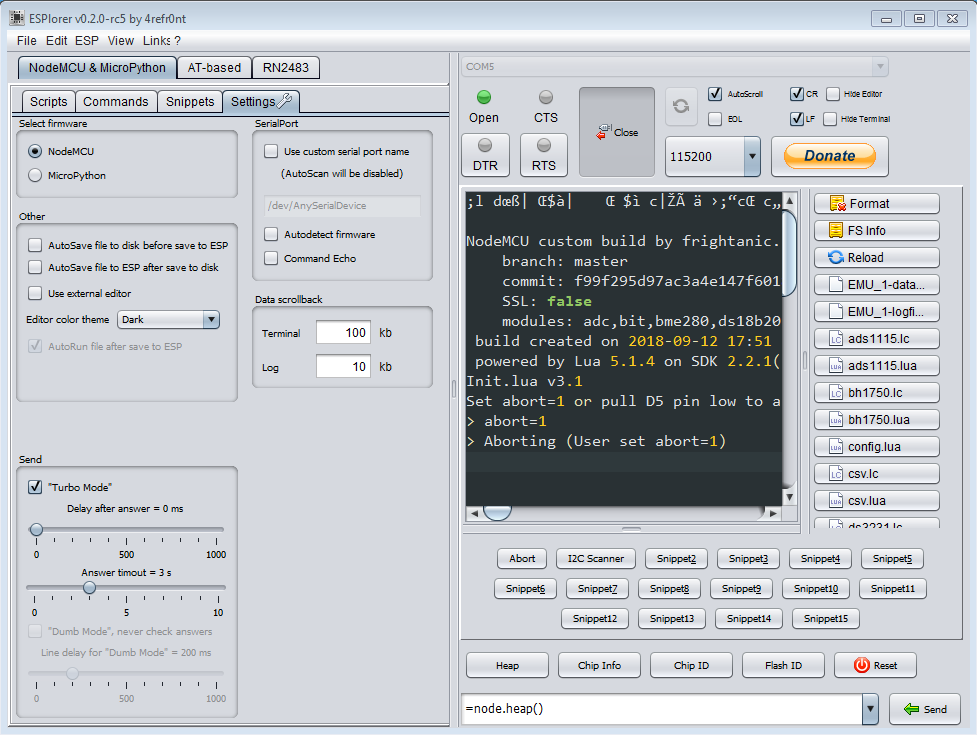
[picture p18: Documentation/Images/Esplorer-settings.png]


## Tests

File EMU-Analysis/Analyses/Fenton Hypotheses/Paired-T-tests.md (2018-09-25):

---
title: "Fenton Paired T-tests"
author: "James Mickley"
output:
  html_document:
    keep_md: yes
    theme: readable
  html_notebook:
    theme: readable
graphics: yes
editor_options: 
  chunk_output_type: console
---

## Overview

Paired T-tests between the two transects.  These pair observations by timestamp and order within the transect.  Any times/orders without paired data are thrown out.  

The difference in means is relative to the Woods transect 

### Temperature

The woods is 1.8 ºC cooler than the meadow

```

	Paired t-test

data:  temperature by transect
t = -26.222, df = 5819, p-value < 2.2e-16
alternative hypothesis: true difference in means is not equal to 0
95 percent confidence interval:
 -1.968443 -1.694588
sample estimates:
mean of the differences 
              -1.831515 
```

### Humidity

The woods is 3.4% more humid than the meadow

```

	Paired t-test

data:  humidity by transect
t = 21.041, df = 5820, p-value < 2.2e-16
alternative hypothesis: true difference in means is not equal to 0
95 percent confidence interval:
 3.119606 3.760637
sample estimates:
mean of the differences 
               3.440122 
```

### PFD

The woods gets less light than the meadow by about 306 µmol/m^2/s

```

	Paired t-test

data:  pfd by transect
t = -56.304, df = 7214, p-value < 2.2e-16
alternative hypothesis: true difference in means is not equal to 0
95 percent confidence interval:
 -316.8756 -295.5530
sample estimates:
mean of the differences 
              -306.2143 
```

### VWC

The woods is drier than the meadow by about 0.13 m^3/m^3

```

	Paired t-test

data:  vwc by transect
t = -178.23, df = 7214, p-value < 2.2e-16
alternative hypothesis: true difference in means is not equal to 0
95 percent confidence interval:
 -0.1387390 -0.1357204
sample estimates:
mean of the differences 
             -0.1372297 
```

### Session Information

```
R version 3.4.3 (2017-11-30)
Platform: x86_64-w64-mingw32/x64 (64-bit)
Running under: Windows 7 x64 (build 7601) Service Pack 1

Matrix products: default

locale:
[1] LC_COLLATE=English_United States.1252 
[2] LC_CTYPE=English_United States.1252   
[3] LC_MONETARY=English_United States.1252
[4] LC_NUMERIC=C                          
[5] LC_TIME=English_United States.1252    

attached base packages:
[1] stats     graphics  grDevices utils     datasets  methods   base     

other attached packages:
 [1] bindrcpp_0.2.2  lubridate_1.7.4 forcats_0.3.0   stringr_1.3.0  
 [5] dplyr_0.7.6     purrr_0.2.4     readr_1.1.1     tidyr_0.8.0    
 [9] tibble_1.4.2    ggplot2_3.0.0   tidyverse_1.2.1

loaded via a namespace (and not attached):
 [1] Rcpp_0.12.16     cellranger_1.1.0 pillar_1.2.2     compiler_3.4.3  
 [5] plyr_1.8.4       bindr_0.1.1      tools_3.4.3      digest_0.6.15   
 [9] jsonlite_1.5     evaluate_0.10.1  nlme_3.1-131     gtable_0.2.0    
[13] lattice_0.20-35  pkgconfig_2.0.1  rlang_0.2.2      psych_1.8.4     
[17] cli_1.0.0        rstudioapi_0.7   yaml_2.1.18      parallel_3.4.3  
[21] haven_1.1.1      withr_2.1.2      xml2_1.2.0       httr_1.3.1      
[25] knitr_1.20       hms_0.4.2        rprojroot_1.3-2  grid_3.4.3      
[29] tidyselect_0.2.4 glue_1.2.0       R6_2.2.2         readxl_1.1.0    
[33] foreign_0.8-69   rmarkdown_1.9    modelr_0.1.1     reshape2_1.4.3  
[37] magrittr_1.5     codetools_0.2-15 backports_1.1.2  scales_0.5.0    
[41] htmltools_0.3.6  rvest_0.3.2      assertthat_0.2.0 mnormt_1.5-5    
[45] colorspace_1.3-2 stringi_1.1.7    lazyeval_0.2.1   munsell_0.4.3   
[49] broom_0.4.4      crayon_1.3.4    
```

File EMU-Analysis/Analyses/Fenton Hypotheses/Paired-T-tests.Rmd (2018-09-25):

---
title: "Fenton Paired T-tests"
author: "James Mickley"
output:
  html_document:
    keep_md: yes
    theme: readable
  html_notebook:
    theme: readable
graphics: yes
editor_options: 
  chunk_output_type: console
---

```{r setup, include = F}
# @@@@@@@@@@@@@@@@@@@@@@@@@@@@@@@@@@@@@@@@@@@@@@@@@@
# @@@@@ Knitr Options
# @@@@@@@@@@@@@@@@@@@@@@@@@@@@@@@@@@@@@@@@@@@@@@@@@@

# Set root directory to the project directory
knitr::opts_knit$set(root.dir = rprojroot::find_rstudio_root_file())

# Set default knitr options: 
# Suppress warnings and messages, cache chunks, 
#  set default figure size to 6x8 at 300 dpi, and save a png and pdf
knitr::opts_chunk$set(warning = F, message = F, collapse = T, cache = T,
    fig.height = 6, fig.width = 8, dpi = 300, # 6x8" @ 300dpi:1800x2400=4.3MP
    dev = c('png', 'pdf'), dev.args = list(pdf = list(onefile = F)))

```

## Overview

Paired T-tests between the two transects.  These pair observations by timestamp and order within the transect.  Any times/orders without paired data are thrown out.  

The difference in means is relative to the Woods transect 

```{r 'Main_Code', include = F, cache = F}

# @@@@@@@@@@@@@@@@@@@@@@@@@@@@@@@@@@@@@@@@@@@@@@@@@@
# @@@@@ Setup - This code is run, but output is hidden
# @@@@@@@@@@@@@@@@@@@@@@@@@@@@@@@@@@@@@@@@@@@@@@@@@@

# Load Packages
require(tidyverse) # Needed for data wrangling
require(lubridate) # Needed for date wrangling

# @@@@@@@@@@@@@@@@@@@@@@@@@@@@@@@@@@@@@@@@@@@@@@@@@@
# @@@@@ Data Preparation
# @@@@@@@@@@@@@@@@@@@@@@@@@@@@@@@@@@@@@@@@@@@@@@@@@@

# Import datasets
data <- read.csv("Data/EMU-6-21/fentondata-all.csv")

```

```{r 'Data_Wrangling', echo = F, include = F}

# Data wrangling on the main dataset
fenton <- data %>%
    
    # Convert the timestamp to a date/time object
    mutate(timestamp = as.POSIXct(timestamp)) %>%
    
    # Remove the seconds from the time, leaving only hour/minute
    mutate(timestamp = timestamp - second(timestamp))

# Take a look at the structure of the main dataset
str(fenton)

```

### Temperature

The woods is 1.8 ºC cooler than the meadow

```{r 'Temperature', echo = F, comment = ""}

# Paired t-test for temperature, based on hourly transect means
#fenton %>%
#    filter(source == "EMU") %>%
#    group_by(transect, hour) %>%
#    summarize(temperature = mean(temperature, na.rm = T)) %>%
#    ungroup %>% data.frame %>% 
#    t.test(temperature ~ transect, paired = T, data = .)

# Paired t-test for temperature
fenton %>%
    
    # Restrict to EMU data
    filter(source == "EMU") %>%

    # Select columns to work with
    select(transect, order, timestamp, temperature) %>%
    
    # Spread, to make one column for each transect
    spread(transect, temperature) %>%
    
    # Remove rows that don't have data for both transects
    filter(!is.na(Meadow), !is.na(Woods)) %>%
    
    # Gather the data back into a transect and temperature column
    gather(transect, temperature, Meadow, Woods) %>%
    
    # Reorder factor levels for transect
    mutate(transect = factor(transect, levels = c("Woods", "Meadow"))) %>%
    
    # Perform paired t-test
    t.test(temperature ~ transect, paired = T, data = .)

```

### Humidity

The woods is 3.4% more humid than the meadow

```{r 'Humidity', echo = F, comment = ""}

# Paired t-test for humidity
fenton %>%
    
    # Restrict to EMU data
    filter(source == "EMU") %>%

    # Select columns to work with
    select(transect, order, timestamp, humidity) %>%
    
    # Spread, to make one column for each transect
    spread(transect, humidity) %>%
    
    # Remove rows that don't have data for both transects
    filter(!is.na(Meadow), !is.na(Woods)) %>%
    
    # Gather the data back into a transect and humidity column
    gather(transect, humidity, Meadow, Woods) %>%
    
    # Reorder factor levels for transect
    mutate(transect = factor(transect, levels = c("Woods", "Meadow"))) %>%
    
    # Perform paired t-test
    t.test(humidity ~ transect, paired = T, data = .)

```

### PFD

The woods gets less light than the meadow by about 306 µmol/m^2/s

```{r 'PAR', echo = F, comment = ""}

# Paired t-test for PFD
fenton %>%
    
    # Restrict to EMU data
    filter(source == "EMU") %>%

    # Select columns to work with
    select(transect, order, timestamp, pfd) %>%
    
    # Spread, to make one column for each transect
    spread(transect, pfd) %>%
    
    # Remove rows that don't have data for both transects
    filter(!is.na(Meadow), !is.na(Woods)) %>%
    
    # Gather the data back into a transect and par column
    gather(transect, pfd, Meadow, Woods) %>%
    
    # Reorder factor levels for transect
    mutate(transect = factor(transect, levels = c("Woods", "Meadow"))) %>%
    
    # Perform paired t-test
    t.test(pfd ~ transect, paired = T, data = .)

```

### VWC

The woods is drier than the meadow by about 0.13 m^3/m^3

```{r 'VWC', echo = F, comment = ""}

# Paired t-test for vwc
fenton %>%
    
    # Restrict to EMU data
    filter(source == "EMU") %>%

    # Select columns to work with
    select(transect, order, timestamp, vwc) %>%
    
    # Spread, to make one column for each transect
    spread(transect, vwc) %>%
    
    # Remove rows that don't have data for both transects
    filter(!is.na(Meadow), !is.na(Woods)) %>%
    
    # Gather the data back into a transect and vwc column
    gather(transect, vwc, Meadow, Woods) %>%
    
    # Reorder factor levels for transect
    mutate(transect = factor(transect, levels = c("Woods", "Meadow"))) %>%
    
    # Perform paired t-test
    t.test(vwc ~ transect, paired = T, data = .)

```

### Session Information

```{r 'Session_Info', echo = F, comment = ""}

# Add session information to help with reproduceability
sessionInfo()

```

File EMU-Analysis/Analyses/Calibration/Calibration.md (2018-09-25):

---
title: "Calibration"
author: "James Mickley"
output:
  html_document:
    keep_md: yes
    theme: readable
    toc: true
  html_notebook:
    theme: readable
graphics: yes
editor_options: 
  chunk_output_type: console
---

### Overview

This analysis calibrates the light and soil moisture sensors.

The light sensor is calibrated for PFD against a LiCor and compared to a Hobo, while the soil probes are calibrated against measured volumetric water content and compared to a Hobo.

### Light Calibration Results

This shows the calibration of the [BH1750FVI light sensor](http://www.mouser.com/ds/2/348/bh1750fvi-e-186247.pdf) against a [LiCor LI-190R Quantum Sensor](https://www.licor.com/env/products/light/quantum.html) connected to a [LiCor LI-250 Light Meter](https://www.licor.com/env/products/light/light_meter.html)

Both were mounted at the same angle and height on a board, and taking readings every second.

#### Light Linear Model

```

Call:
lm(formula = umol ~ lux, data = light)

Residuals:
     Min       1Q   Median       3Q      Max 
-178.248  -37.350   -9.541   45.492  113.408 

Coefficients:
             Estimate Std. Error t value Pr(>|t|)    
(Intercept) 5.919e+01  9.603e+00   6.164 1.25e-08 ***
lux         1.675e-02  1.465e-04 114.378  < 2e-16 ***
---
Signif. codes:  0 '***' 0.001 '**' 0.01 '*' 0.05 '.' 0.1 ' ' 1

Residual standard error: 56.45 on 108 degrees of freedom
Multiple R-squared:  0.9918,	Adjusted R-squared:  0.9917 
F-statistic: 1.308e+04 on 1 and 108 DF,  p-value: < 2.2e-16
```

#### Light Quadratic Model

```

Call:
lm(formula = umol ~ lux + lux.squared, data = .)

Residuals:
     Min       1Q   Median       3Q      Max 
-203.442  -24.529   -1.738   38.084  100.974 

Coefficients:
              Estimate Std. Error t value Pr(>|t|)    
(Intercept)  2.239e+01  1.180e+01   1.899   0.0603 .  
lux          1.893e-02  4.849e-04  39.047  < 2e-16 ***
lux.squared -1.898e-08  4.057e-09  -4.679 8.49e-06 ***
---
Signif. codes:  0 '***' 0.001 '**' 0.01 '*' 0.05 '.' 0.1 ' ' 1

Residual standard error: 51.67 on 107 degrees of freedom
Multiple R-squared:  0.9932,	Adjusted R-squared:  0.9931 
F-statistic:  7817 on 2 and 107 DF,  p-value: < 2.2e-16
```

#### Light Calibration Graphs

Comparison between the linear and quadratic models

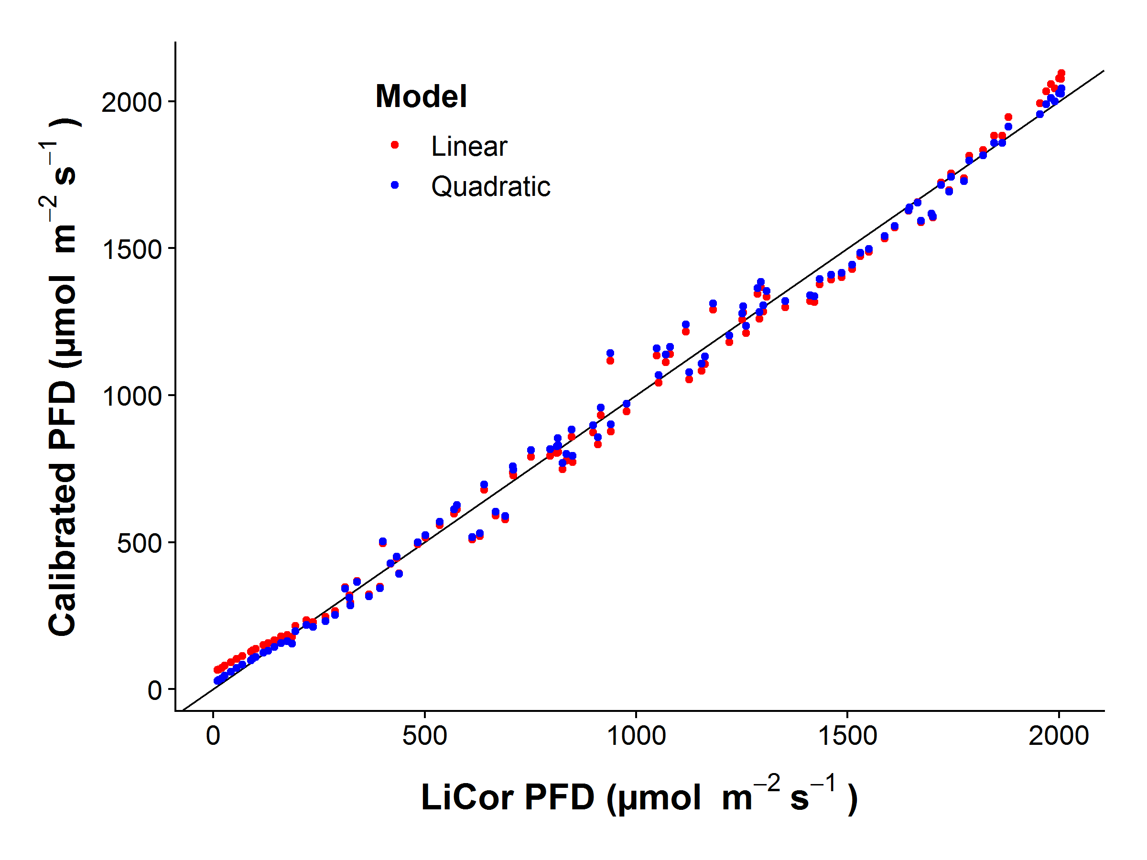
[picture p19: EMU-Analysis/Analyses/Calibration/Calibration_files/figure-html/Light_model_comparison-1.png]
<!-- -->

The best calibration is the quadratic model, presented here alone

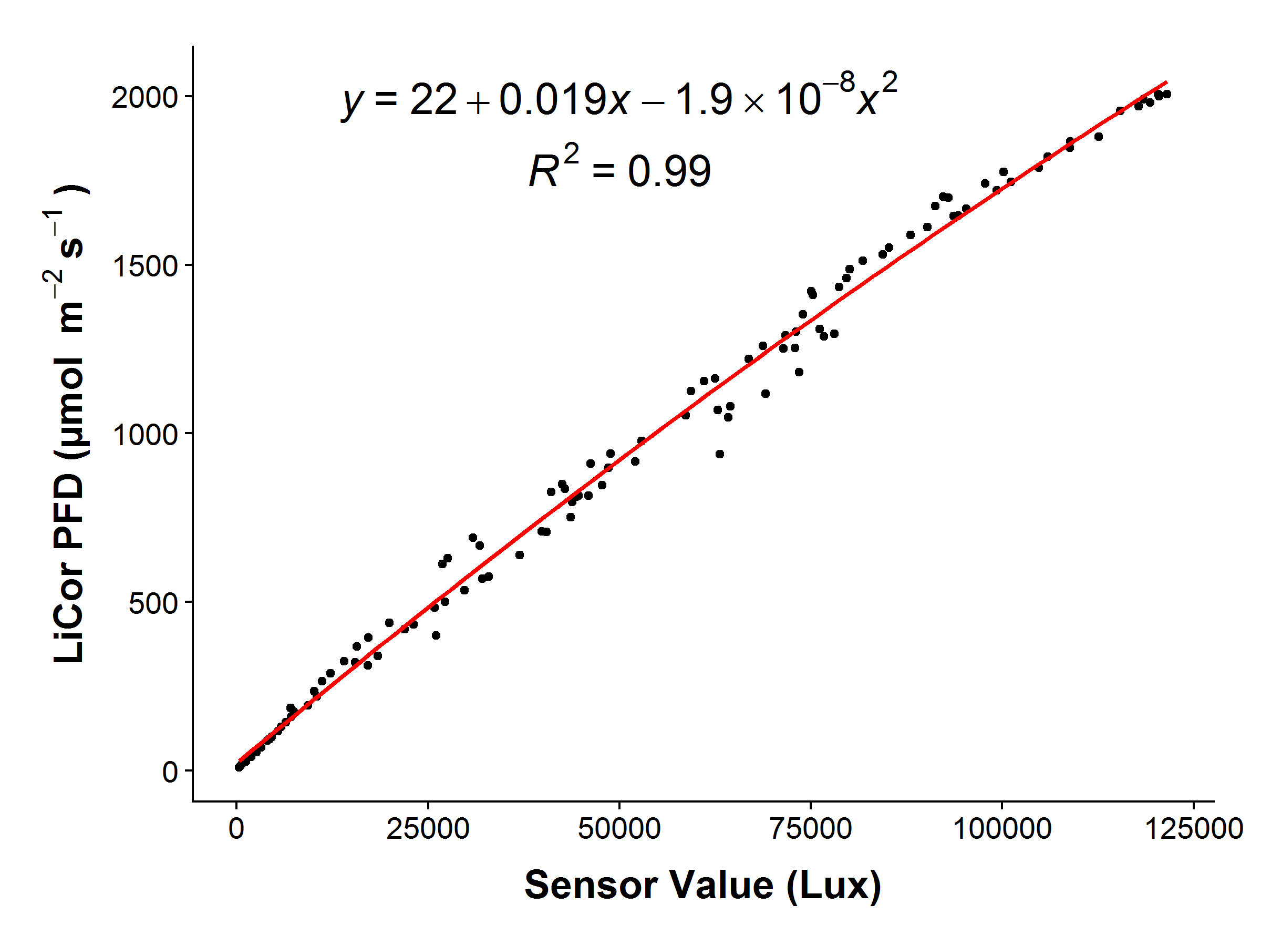
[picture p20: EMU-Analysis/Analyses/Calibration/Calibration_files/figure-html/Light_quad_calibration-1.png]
<!-- -->

[Root mean square](https://en.wikipedia.org/wiki/Root_mean_square#Error) error between predicted values from the quadratic light model and PFD values from the LiCor.  This gives a measure of accuracy.

```
  mean.square root.mean.square
1    2597.424         50.96493
```

Graph showing the predicted values of PFD from the quadratic model graphed against the LiCor

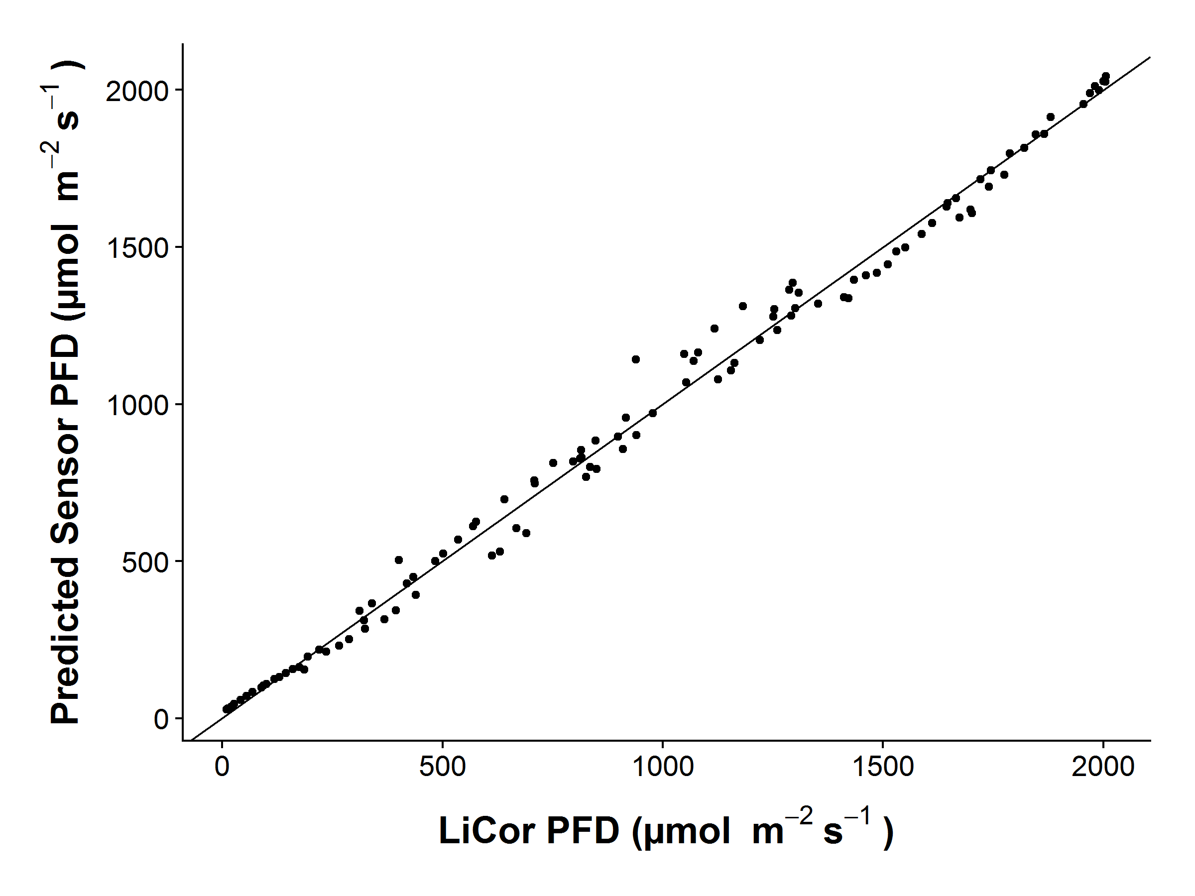
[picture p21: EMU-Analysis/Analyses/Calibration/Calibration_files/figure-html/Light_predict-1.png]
<!-- -->

### Soil Calibration Results

Calibration of generic silver and gold soil moisture sensor probes with a datalogging scale, measuring water content of the soil every five minutes. The soil used for calibration was a rich loam from the Fenton Meadow. The data columns soil1 and soil2 are gold (ENIG) probes, while soil3 is a silver (HASL) probe.

### Soil Gold Models

Models using the data from the gold-plated soil moisture probe

#### Soil Gold Linear Model

```

Call:
lm(formula = vwc ~ gold, data = .)

Residuals:
      Min        1Q    Median        3Q       Max 
-0.023981 -0.010827  0.001181  0.008224  0.044489 

Coefficients:
              Estimate Std. Error t value Pr(>|t|)    
(Intercept)  3.597e-01  5.311e-04   677.3   <2e-16 ***
gold        -1.296e-05  2.850e-08  -454.6   <2e-16 ***
---
Signif. codes:  0 '***' 0.001 '**' 0.01 '*' 0.05 '.' 0.1 ' ' 1

Residual standard error: 0.01277 on 7678 degrees of freedom
Multiple R-squared:  0.9642,	Adjusted R-squared:  0.9642 
F-statistic: 2.067e+05 on 1 and 7678 DF,  p-value: < 2.2e-16
```

#### Soil Gold Quadratic Model

The quadratic model is considerably better

```

Call:
lm(formula = vwc ~ gold + gold.squared, data = .)

Residuals:
       Min         1Q     Median         3Q        Max 
-0.0154048 -0.0034169 -0.0000345  0.0035356  0.0142257 

Coefficients:
               Estimate Std. Error t value Pr(>|t|)    
(Intercept)   4.806e-01  7.129e-04   674.2   <2e-16 ***
gold         -2.887e-05  8.951e-08  -322.5   <2e-16 ***
gold.squared  4.727e-10  2.633e-12   179.5   <2e-16 ***
---
Signif. codes:  0 '***' 0.001 '**' 0.01 '*' 0.05 '.' 0.1 ' ' 1

Residual standard error: 0.005603 on 7677 degrees of freedom
Multiple R-squared:  0.9931,	Adjusted R-squared:  0.9931 
F-statistic: 5.53e+05 on 2 and 7677 DF,  p-value: < 2.2e-16
          dAICc   df
gold.quad     0.0 4 
gold.lm   12654.2 3 
```

#### Soil Gold Quadratic Temperature Model

The quadratic temperature-compensated model is better by AIC, but it doesn't add much, and doesn't eliminate the residual zig-zag pattern (see below).

```

Call:
lm(formula = vwc ~ gold + gold.squared + temp, data = .)

Residuals:
       Min         1Q     Median         3Q        Max 
-0.0135034 -0.0027853  0.0007276  0.0033035  0.0138653 

Coefficients:
               Estimate Std. Error t value Pr(>|t|)    
(Intercept)   5.656e-01  1.323e-03  427.63   <2e-16 ***
gold         -3.080e-05  7.480e-08 -411.72   <2e-16 ***
gold.squared  5.302e-10  2.204e-12  240.51   <2e-16 ***
temp         -2.720e-03  3.844e-05  -70.74   <2e-16 ***
---
Signif. codes:  0 '***' 0.001 '**' 0.01 '*' 0.05 '.' 0.1 ' ' 1

Residual standard error: 0.00436 on 7676 degrees of freedom
Multiple R-squared:  0.9958,	Adjusted R-squared:  0.9958 
F-statistic: 6.106e+05 on 3 and 7676 DF,  p-value: < 2.2e-16
               dAICc   df
gold.quad.temp     0.0 5 
gold.quad       3853.1 4 
gold.lm        16507.3 3 
```

### Soil Gold Models

Models using the data from the silver (solder plated) soil moisture probe

#### Soil Silver Linear Model

```

Call:
lm(formula = vwc ~ silver, data = .)

Residuals:
       Min         1Q     Median         3Q        Max 
-0.0180007 -0.0061523  0.0002036  0.0057225  0.0272827 

Coefficients:
              Estimate Std. Error t value Pr(>|t|)    
(Intercept)  4.341e-01  4.153e-04  1045.3   <2e-16 ***
silver      -1.513e-05  2.002e-08  -755.6   <2e-16 ***
---
Signif. codes:  0 '***' 0.001 '**' 0.01 '*' 0.05 '.' 0.1 ' ' 1

Residual standard error: 0.007773 on 7678 degrees of freedom
Multiple R-squared:  0.9867,	Adjusted R-squared:  0.9867 
F-statistic: 5.71e+05 on 1 and 7678 DF,  p-value: < 2.2e-16
```

#### Soil Silver Quadratic Model

```

Call:
lm(formula = vwc ~ silver + silver.squared, data = .)

Residuals:
      Min        1Q    Median        3Q       Max 
-0.019434 -0.003896  0.000419  0.004251  0.014139 

Coefficients:
                 Estimate Std. Error t value Pr(>|t|)    
(Intercept)     5.165e-01  1.288e-03   401.0   <2e-16 ***
silver         -2.460e-05  1.440e-07  -170.9   <2e-16 ***
silver.squared  2.546e-10  3.846e-12    66.2   <2e-16 ***
---
Signif. codes:  0 '***' 0.001 '**' 0.01 '*' 0.05 '.' 0.1 ' ' 1

Residual standard error: 0.006202 on 7677 degrees of freedom
Multiple R-squared:  0.9916,	Adjusted R-squared:  0.9916 
F-statistic: 4.506e+05 on 2 and 7677 DF,  p-value: < 2.2e-16
            dAICc  df
silver.quad    0.0 4 
silver.lm   3466.7 3 
```

#### Soil Silver Quadratic Temperature Model

```

Call:
lm(formula = vwc ~ silver + silver.squared + temp, data = .)

Residuals:
       Min         1Q     Median         3Q        Max 
-0.0164454 -0.0030356  0.0007289  0.0036374  0.0134823 

Coefficients:
                 Estimate Std. Error t value Pr(>|t|)    
(Intercept)     6.188e-01  1.722e-03  359.35   <2e-16 ***
silver         -2.737e-05  1.172e-07 -233.60   <2e-16 ***
silver.squared  3.281e-10  3.128e-12  104.89   <2e-16 ***
temp           -3.008e-03  4.138e-05  -72.68   <2e-16 ***
---
Signif. codes:  0 '***' 0.001 '**' 0.01 '*' 0.05 '.' 0.1 ' ' 1

Residual standard error: 0.004774 on 7676 degrees of freedom
Multiple R-squared:  0.995,	Adjusted R-squared:  0.995 
F-statistic: 5.088e+05 on 3 and 7676 DF,  p-value: < 2.2e-16
                 dAICc  df
silver.quad.temp    0.0 5 
silver.lm        7486.2 3 
```

#### Soil Calibration Graphs

Showing soil moisture probe values over time. There is some diurnal variation that is partially temperature-driven.

Adding temperature to the quadratic fit does improve things slightly, but the temperature range is only ~21-30 C, so it doesn't encompass the full temperature range outside

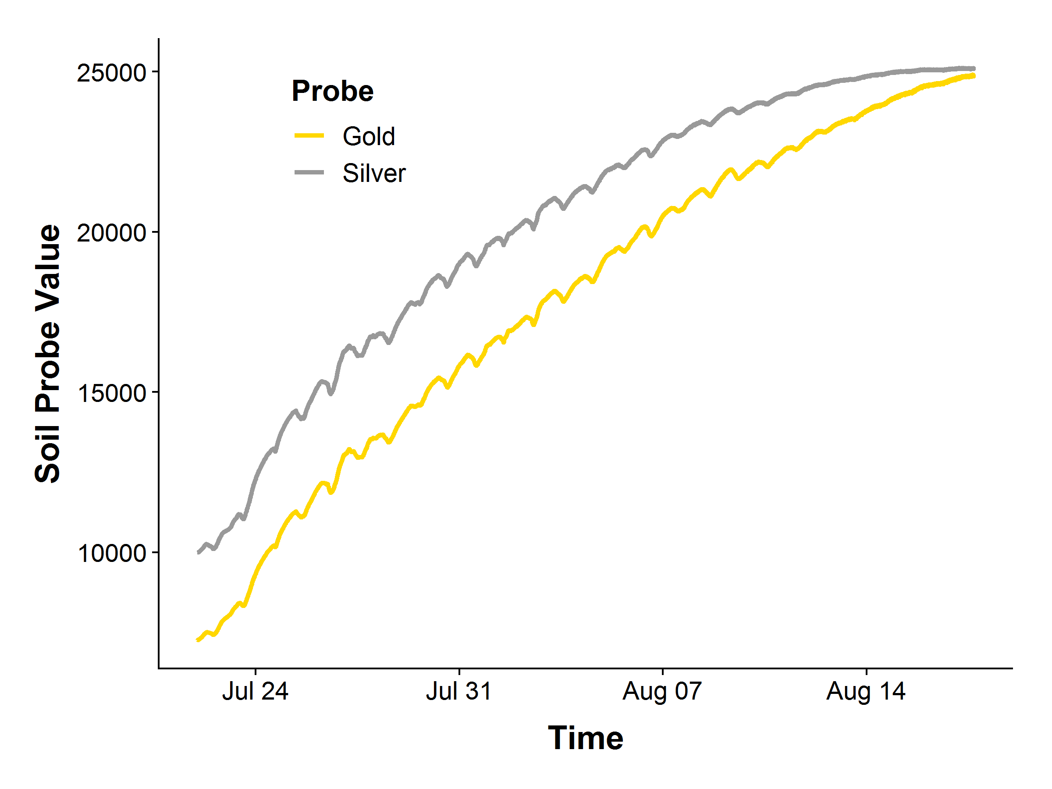
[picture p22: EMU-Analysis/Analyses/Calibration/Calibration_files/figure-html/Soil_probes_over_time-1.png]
<!-- -->

[Root mean square](https://en.wikipedia.org/wiki/Root_mean_square#Error) error between predicted values from the gold probe quadratic model and measured VWC values from the scale.  This gives a measure of accuracy.

```
  mean.square root.mean.square
1  0.00604131       0.07772586
```

A graph of the calibration and formula using the quadratic model for the gold probe

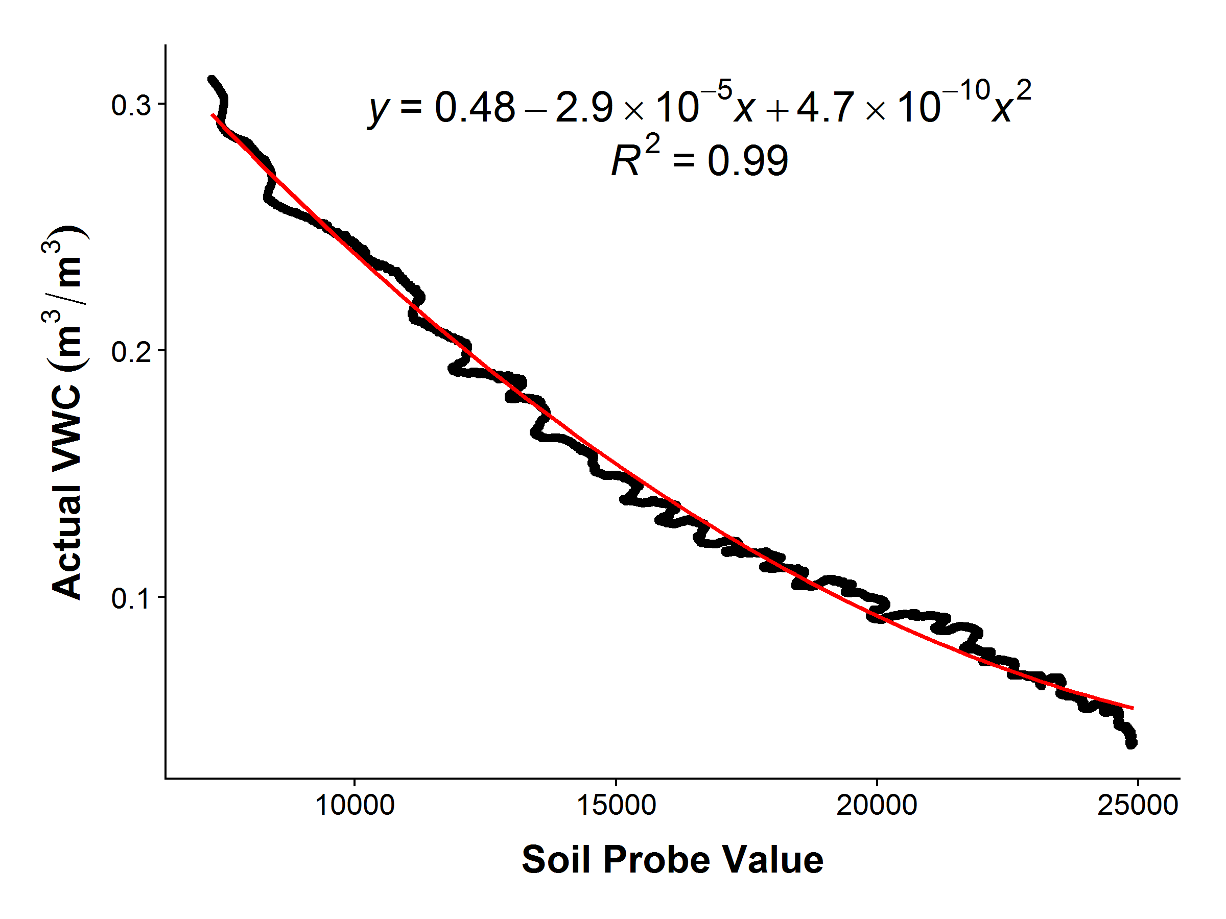
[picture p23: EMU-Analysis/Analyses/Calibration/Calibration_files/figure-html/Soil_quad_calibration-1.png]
<!-- -->

Graph showing the predicted values of VWC from the quadratic model graphed against the actual VWC. Notably, the zig-zag pattern improves slightly in the temperature-compensated model, but it is far from eliminated.

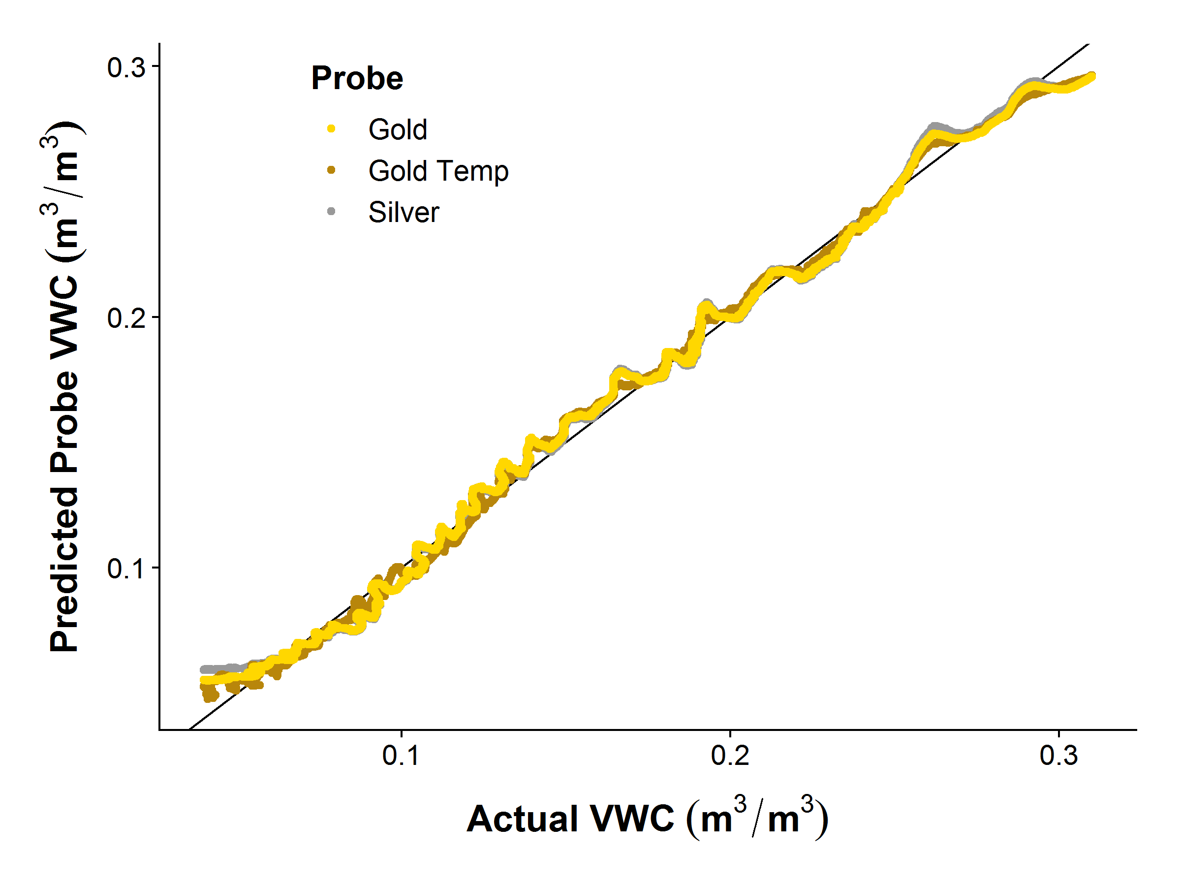
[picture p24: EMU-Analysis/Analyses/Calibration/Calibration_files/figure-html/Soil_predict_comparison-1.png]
<!-- -->

### Session Information

```
R version 3.4.3 (2017-11-30)
Platform: x86_64-w64-mingw32/x64 (64-bit)
Running under: Windows 7 x64 (build 7601) Service Pack 1

Matrix products: default

locale:
[1] LC_COLLATE=English_United States.1252 
[2] LC_CTYPE=English_United States.1252   
[3] LC_MONETARY=English_United States.1252
[4] LC_NUMERIC=C                          
[5] LC_TIME=English_United States.1252    

attached base packages:
[1] stats4    stats     graphics  grDevices utils     datasets  methods  
[8] base     

other attached packages:
 [1] bindrcpp_0.2.2  bbmle_1.0.20    ggpmisc_0.3.0   cowplot_0.9.3  
 [5] forcats_0.3.0   stringr_1.3.0   dplyr_0.7.6     purrr_0.2.4    
 [9] readr_1.1.1     tidyr_0.8.0     tibble_1.4.2    ggplot2_3.0.0  
[13] tidyverse_1.2.1

loaded via a namespace (and not attached):
 [1] tidyselect_0.2.4  reshape2_1.4.3    haven_1.1.1      
 [4] lattice_0.20-35   colorspace_1.3-2  htmltools_0.3.6  
 [7] yaml_2.1.18       rlang_0.2.2       pillar_1.2.2     
[10] foreign_0.8-69    glue_1.2.0        withr_2.1.2      
[13] modelr_0.1.1      readxl_1.1.0      bindr_0.1.1      
[16] plyr_1.8.4        munsell_0.4.3     gtable_0.2.0     
[19] cellranger_1.1.0  rvest_0.3.2       codetools_0.2-15 
[22] psych_1.8.4       evaluate_0.10.1   labeling_0.3     
[25] knitr_1.20        parallel_3.4.3    broom_0.4.4      
[28] Rcpp_0.12.16      polynom_1.3-9     scales_0.5.0     
[31] backports_1.1.2   jsonlite_1.5      mnormt_1.5-5     
[34] hms_0.4.2         digest_0.6.15     stringi_1.1.7    
[37] numDeriv_2016.8-1 grid_3.4.3        rprojroot_1.3-2  
[40] cli_1.0.0         tools_3.4.3       magrittr_1.5     
[43] lazyeval_0.2.1    crayon_1.3.4      pkgconfig_2.0.1  
[46] xml2_1.2.0        lubridate_1.7.4   assertthat_0.2.0 
[49] rmarkdown_1.9     httr_1.3.1        rstudioapi_0.7   
[52] R6_2.2.2          nlme_3.1-131      compiler_3.4.3   
```

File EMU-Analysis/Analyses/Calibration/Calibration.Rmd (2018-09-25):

---
title: "Calibration"
author: "James Mickley"
output:
  html_document:
    keep_md: yes
    theme: readable
    toc: true
  html_notebook:
    theme: readable
graphics: yes
editor_options: 
  chunk_output_type: console
---

```{r setup, include = F}
# @@@@@@@@@@@@@@@@@@@@@@@@@@@@@@@@@@@@@@@@@@@@@@@@@@
# @@@@@ Knitr Options
# @@@@@@@@@@@@@@@@@@@@@@@@@@@@@@@@@@@@@@@@@@@@@@@@@@

# Set root directory to the project directory
knitr::opts_knit$set(root.dir = rprojroot::find_rstudio_root_file())

# Set default knitr options: 
# Suppress warnings and messages, cache chunks, 
#  set default figure size to 6x8 at 300 dpi, and save a png and pdf
knitr::opts_chunk$set(warning = F, message = F, collapse = T, cache = T,
    fig.height = 6, fig.width = 8, dpi = 300, # 6x8" @ 300dpi:1800x2400=4.3MP
    dev = c('png', 'pdf'), dev.args = list(pdf = list(onefile = F)))

```

### Overview

This analysis calibrates the light and soil moisture sensors.

The light sensor is calibrated for PFD against a LiCor and compared to a Hobo, while the soil probes are calibrated against measured volumetric water content and compared to a Hobo.

```{r 'Main_Code', include = F, cache = F}

# @@@@@@@@@@@@@@@@@@@@@@@@@@@@@@@@@@@@@@@@@@@@@@@@@@
# @@@@@ Setup - This code is run, but output is hidden
# @@@@@@@@@@@@@@@@@@@@@@@@@@@@@@@@@@@@@@@@@@@@@@@@@@

# Load Packages
require(tidyverse) # Needed for ggplot2 and data wrangling
require(cowplot) # Needed for publication-quality ggplots
require(ggpmisc) # Needed for lm equations on graphs
require(bbmle) # Needed for AICctab

# @@@@@@@@@@@@@@@@@@@@@@@@@@@@@@@@@@@@@@@@@@@@@@@@@@
# @@@@@ Data Preparation
# @@@@@@@@@@@@@@@@@@@@@@@@@@@@@@@@@@@@@@@@@@@@@@@@@@

# Import datasets
light <- read.csv("Data/licor-calibration/licor-calibration.csv")
soil <- read.csv("Data/Fenton-soil/Fenton_soil_calibration.csv")

# @@@@@@@@@@@@@@@@@@@@@@@@@@@@@@@@@@@@@@@@@@@@@@@@@@
# @@@@@ ggPlot Theme
# @@@@@@@@@@@@@@@@@@@@@@@@@@@@@@@@@@@@@@@@@@@@@@@@@@

ggplot.theme <- theme(
    
    # Text size for axis ticks
    axis.text.y = element_text(size = 14),
    axis.text.x = element_text(size = 14),
    
    # Text size for axis labels
    # Also move them away from the axes a bit for more space
    axis.title.x = element_text(size = 18, face = "bold", vjust = -1),
    axis.title.y = element_text(size = 18, face = "bold", vjust = 1.5),
    
    # Plot title size
    plot.title = element_text(size = 20, face = "bold"),
    
    # Margins for top, right, bottom, left
    plot.margin = grid::unit(c(1.5, 1.5, 1.5, 1.2), "lines"), 
    
    # Legend text size
    legend.text = element_text(size = 14),
    legend.text.align = 0, 
    legend.title = element_text(size = 16, face = "bold"),
    legend.key.size = grid::unit(1.4, "line"),
    legend.key = element_blank()
    )

```

### Light Calibration Results

This shows the calibration of the [BH1750FVI light sensor](http://www.mouser.com/ds/2/348/bh1750fvi-e-186247.pdf) against a [LiCor LI-190R Quantum Sensor](https://www.licor.com/env/products/light/quantum.html) connected to a [LiCor LI-250 Light Meter](https://www.licor.com/env/products/light/light_meter.html)

Both were mounted at the same angle and height on a board, and taking readings every second.

#### Light Linear Model

```{r 'Light_linear_model', echo = F, comment = ""}

# Run a linear model
light.lm <- lm(umol ~ lux, data = light)

# Show summary
summary(light.lm)

```

#### Light Quadratic Model

```{r 'Light_quadratic_model', echo = F, comment = ""}

# Run a quadratic model
light.quad <- light %>%

    # Add a squared column
    mutate(lux.squared = lux ^ 2) %>%
    
    # model
    lm(umol ~ lux + lux.squared, data = .)

# Show summary
summary(light.quad)

# Rename the intercept coefficient
names(light.quad$coefficients)[1] <- "intercept"

# Write the calibration coefficients to a CSV
write.csv(data.frame(as.list(light.quad$coefficients)),
    "Analyses/Calibration/light-calibration.csv", row.names = F)

```

```{r 'Predict_Light', echo = F, include = F}

# Update the dataset with predicted values from the linear models
light <- light %>%
    
    # Add the linear calibration
    mutate(umol.linear = light.lm$coefficients[1] + 
        light.lm$coefficients[2] * lux) %>%
    
    # Add the quadratic calibration
    mutate(umol.quad = light.quad$coefficients[1] + 
        light.quad$coefficients[2] * lux + 
        light.quad$coefficients[3] * lux ^ 2)

```

#### Light Calibration Graphs

Comparison between the linear and quadratic models

```{r 'Light_model_comparison', echo = F}

light %>%
    
    # Make a column with both the linear and quad predicted values
    gather(calibration, value, umol.linear, umol.quad) %>%
    
    # Construct the graph
    ggplot(aes(x = umol, y = value, color = calibration)) +
    
        # Add a line with a slope of 1 and intercept of 0
        geom_abline(intercept = 0, slope = 1) + 

        # Add points
        geom_point() +
    
        # 
        scale_color_manual(name = "Model", labels = c("Linear", "Quadratic"), 
            values = c("red", "blue")) +
    
        # Add axes
        xlab(bquote(bold('LiCor PFD (µmol '~m^-2 ~s^-1~')'))) +
        ylab(bquote(bold('Calibrated PFD (µmol '~m^-2 ~s^-1~')'))) +
    
        # Add theme
        ggplot.theme + 
    
        # Move the legend
        theme(legend.position = c(0.2, 0.85))

```

The best calibration is the quadratic model, presented here alone

```{r 'Light_quad_calibration', echo = F}

# Construct the graph
light %>% ggplot(aes(x = lux, y = umol)) +
    
        # Add points
        geom_point() +
    
        # Add linear model
        geom_smooth(method = "lm", color = "red", se = F, 
            formula = y ~ poly(x, 2, raw = T)) + 
    
        # Add the equation
        stat_poly_eq(aes(label = ..eq.label..),
               eq.x.rhs = "italic(x)", coef.digits = 2, label.x = 50000, 
               label.y = 2000, parse = T, size = 7,
               formula = y ~ poly(x, 2, raw = T)) +
        
        # Add the R^2
        stat_poly_eq(aes(label = ..rr.label..),
               coef.digits = 2, label.x = 50000, label.y = 1800,
               parse = T, size = 7, formula = y ~ poly(x, 2, raw = T)) +
    
        # Add axes
        ylab(bquote(bold('LiCor PFD (µmol '~m^-2 ~s^-1~')'))) +
        xlab("Sensor Value (Lux)") +
    
        # Add theme
        ggplot.theme

```

[Root mean square](https://en.wikipedia.org/wiki/Root_mean_square#Error) error between predicted values from the quadratic light model and PFD values from the LiCor.  This gives a measure of accuracy.

```{r 'RMSE_Light', echo = F, comment = ""}

# Calculate the root mean square of the residuals
rms.light <- light %>%
    
    # Calculate the difference between the LiCor and the prediction
    mutate(umol.diff = umol - umol.quad) %>%
    
    # Square the differences
    mutate(diff.squared = umol.diff ^ 2) %>%
    
    # Calculate the mean square and root mean square
    summarize(mean.square = mean(diff.squared), 
        root.mean.square = sqrt(mean.square))

# Display
rms.light

```

Graph showing the predicted values of PFD from the quadratic model graphed against the LiCor

```{r 'Light_predict', echo = F}

#TODO: Add equation to graph

# Construct the graph
light %>% ggplot(aes(x = umol, y = umol.quad)) +
    
        # Add a line with a slope of 1 and intercept of 0
        geom_abline(intercept = 0, slope = 1) + 
    
        # Add points
        geom_point() +
    
        # Add axes
        xlab(bquote(bold('LiCor PFD (µmol '~m^-2 ~s^-1~')'))) +
        ylab(bquote(bold('Predicted Sensor PFD (µmol '~m^-2 ~s^-1~')'))) +
    
        # Add theme
        ggplot.theme

```

### Soil Calibration Results

Calibration of generic silver and gold soil moisture sensor probes with a datalogging scale, measuring water content of the soil every five minutes. The soil used for calibration was a rich loam from the Fenton Meadow. The data columns soil1 and soil2 are gold (ENIG) probes, while soil3 is a silver (HASL) probe.

```{r 'Data_Wrangling_Soil', echo = F, comment = ""}

# From the metadata
fenton.dryweight = 992.7
fenton.wetweight = 1638.7
fenton.density = 0.90

# Data wrangling
cal <- soil %>%

    # Remove the metadata column
    select(-metadata) %>%
    
    # Get rid of any missing data rows
    filter(!is.na(weight)) %>%
    
    # Add columns for measured gravimetric and volumetric water content
    mutate(gwc = (weight - fenton.dryweight) / fenton.dryweight, 
        vwc = gwc * fenton.density) %>%
    
    # Convert the date to date format
    mutate(date = as.POSIXct(date, format = "%m/%d/%Y %H:%M"))

```

### Soil Gold Models

Models using the data from the gold-plated soil moisture probe

#### Soil Gold Linear Model

```{r 'Soil_linear_gold_model', echo = F, comment = ""}

# Calibrate the gold probes using a simple linear model
gold.lm <- cal %>%
    
    # Filter for after 7/22, when probes hit a minimum
    filter(date >= as.POSIXct("2017-07-22 00:00")) %>%
    
    # Run the linear model
    lm(vwc ~ gold, data = .)

# View the model
summary(gold.lm)

```

#### Soil Gold Quadratic Model

The quadratic model is considerably better

```{r 'Soil_quadratic_gold_model', echo = F, comment = ""}

# Calibrate the gold probes using a quadratic model
gold.quad <- cal %>%
  
    # Filter for after 7/22, when probes hit a minimum
    filter(date >= as.POSIXct("2017-07-22 00:00")) %>%
    
    # Make a squared column
    mutate(gold.squared = gold ^ 2) %>%

    # Run the quadratic model
    lm(vwc ~ gold + gold.squared, data = .)
 
# View the model
summary(gold.quad)

# Check AICsh
AICctab(gold.lm, gold.quad)

# Rename the intercept coefficient
names(gold.quad$coefficients) <- c("intercept", "soil", "soil.squared")

# Write the calibration coefficients to a CSV
write.csv(data.frame(as.list(gold.quad$coefficients)),
    "Analyses/Calibration/gold-soil-calibration.csv", row.names = F)

```

#### Soil Gold Quadratic Temperature Model

The quadratic temperature-compensated model is better by AIC, but it doesn't add much, and doesn't eliminate the residual zig-zag pattern (see below).

```{r 'Soil_quadratic_gold_temp_model', echo = F, comment = ""}

# Calibrate the gold probes using a quadratic model
gold.quad.temp <- cal %>%
  
    # Filter for after 7/22, when probes hit a minimum
    filter(date >= as.POSIXct("2017-07-22 00:00")) %>%
    
    # Make a squared column
    mutate(gold.squared = gold ^ 2) %>%

    # Run the quadratic model
    lm(vwc ~ gold + gold.squared + temp, data = .)
 
# View the model
summary(gold.quad.temp)

# Check AICsh
AICctab(gold.lm, gold.quad, gold.quad.temp)

```

### Soil Gold Models

Models using the data from the silver (solder plated) soil moisture probe

#### Soil Silver Linear Model

```{r 'Soil_linear_silver_model', echo = F, comment = ""}

# Calibrate the silver probe using a simple linear model
silver.lm <- cal %>%
    
    # Filter for after 7/22, when probes hit a minimum
    filter(date >= as.POSIXct("2017-07-22 00:00")) %>%
    
    # Run the linear model
    lm(vwc ~ silver, data = .)

# View the model
summary(silver.lm)

```

#### Soil Silver Quadratic Model

```{r 'Soil_quadratic_silver_model', echo = F, comment = ""}

# Calibrate the silver probe using a quadratic model
silver.quad <- cal %>%
    
    # Filter for after 7/22, when probes hit a minimum
    filter(date >= as.POSIXct("2017-07-22 00:00")) %>%
    
    # Make a squared column
    mutate(silver.squared = silver ^ 2) %>%
    
    # Run the linear model
    lm(vwc ~ silver + silver.squared, data = .)

# View the model
summary(silver.quad)

# Check AICc
AICctab(silver.lm, silver.quad)

# Rename the intercept coefficient
names(silver.quad$coefficients) <- c("intercept", "soil", "soil.squared")

# Write the calibration coefficients to a CSV
write.csv(data.frame(as.list(silver.quad$coefficients)),
    "Analyses/Calibration/silver-soil-calibration.csv", row.names = F)

```

#### Soil Silver Quadratic Temperature Model

```{r 'Soil_quadratic_silver_temp_model', echo = F, comment = ""}

# Calibrate the silver probe using a quadratic model
silver.quad.temp <- cal %>%
    
    # Filter for after 7/22, when probes hit a minimum
    filter(date >= as.POSIXct("2017-07-22 00:00")) %>%
    
    # Make a squared column
    mutate(silver.squared = silver ^ 2) %>%
    
    # Run the linear model
    lm(vwc ~ silver + silver.squared + temp, data = .)

# View the model
summary(silver.quad.temp)

# Check AICc
AICctab(silver.lm, silver.quad.temp)

```

```{r 'Predict_Soil', echo = F, include = F}

# Update the dataset with predicted values from the linear models
cal <- cal %>%
    
    # Add the quadratic calibration for the gold probe
    mutate(gold_vwc = gold.quad$coefficients[1] + 
        gold.quad$coefficients[2] * gold + 
        gold.quad$coefficients[3] * gold ^ 2) %>%
    
    # Add the temperature compensated quadratic calibration for the gold probe
    mutate(gold_vwc_temp = gold.quad.temp$coefficients[1] + 
        gold.quad.temp$coefficients[2] * gold + 
        gold.quad.temp$coefficients[3] * gold ^ 2 + 
        gold.quad.temp$coefficients[4] * temp) %>%
    
    # Add the quadratic calibration for the silver probe
    mutate(silver_vwc = silver.quad$coefficients[1] + 
        silver.quad$coefficients[2] * silver + 
        silver.quad$coefficients[3] * silver ^ 2) %>%

    # Add the temperature compensated quadratic calibration for the silver probe
    mutate(silver_vwc_temp = silver.quad.temp$coefficients[1] + 
        silver.quad.temp$coefficients[2] * silver + 
        silver.quad.temp$coefficients[3] * silver ^ 2 + 
        silver.quad.temp$coefficients[4] * temp)

```

#### Soil Calibration Graphs

Showing soil moisture probe values over time. There is some diurnal variation that is partially temperature-driven.

Adding temperature to the quadratic fit does improve things slightly, but the temperature range is only ~21-30 C, so it doesn't encompass the full temperature range outside

```{r 'Soil_probes_over_time', echo = F}

cal %>%
    
    # Filter for after 7/22, when probes hit a minimum
    filter(date >= as.POSIXct("2017-07-22 00:00")) %>%
    
    gather(probe, value, gold, silver) %>%

    ggplot(aes(x = date, y = value, color = probe, group = probe)) +

        # Set up the colors and legend
        scale_color_manual(values = c("gold", "gray60"), name = "Probe", 
            labels = c("Gold", "Silver")) +
    
        geom_line(size = 1.2) +
    
        xlab("Time") +
        ylab("Soil Probe Value") + 
    
        # Add theme
        ggplot.theme + 
    
        # Change legend position
        theme(legend.position = c(0.14, 0.85))

```

[Root mean square](https://en.wikipedia.org/wiki/Root_mean_square#Error) error between predicted values from the gold probe quadratic model and measured VWC values from the scale.  This gives a measure of accuracy.

```{r 'RMSE_Soil', echo = F, comment = ""}

# Calculate the root mean square of the residuals
rms.soil <- cal %>%
    
    # Calculate the difference between the actual VWC and the prediction
    mutate(vwc.diff = vwc - gold_vwc) %>%
    
    # Square the differences
    mutate(diff.squared = vwc.diff ^ 2) %>%
    
    # Calculate the mean square and root mean square
    summarize(mean.square = mean(diff.squared), 
        root.mean.square = sqrt(mean.square))

# Display
rms.soil

```

A graph of the calibration and formula using the quadratic model for the gold probe

```{r 'Soil_quad_calibration', echo = F}

cal %>%
    
    # Filter for after 7/22, when probes hit a minimum
    filter(date >= as.POSIXct("2017-07-22 00:00")) %>%

    ggplot(aes(x = gold, y = vwc)) +
    
        # Add points
        geom_point() + 
    
        # Add linear model
        geom_smooth(method = "lm", color = "red", se = F, 
            formula = y ~ poly(x, 2, raw = T)) + 
    
        # Add the equation
        stat_poly_eq(aes(label = ..eq.label..),
               eq.x.rhs = "italic(x)", coef.digits = 2, label.x = 16600, 
               label.y = 0.30, parse = T, size = 7,
               formula = y ~ poly(x, 2, raw = T)) +
        
        # Add the R^2
        stat_poly_eq(aes(label = ..rr.label..),
               coef.digits = 2, label.x = 16600, label.y = 0.28,
               parse = T, size = 7, formula = y ~ poly(x, 2, raw = T)) +
    
        # Add axis labels
        xlab("Soil Probe Value") + 
        ylab(bquote(bold('Actual VWC'~(m^3/m^3)))) +
    
        # Add theme
        ggplot.theme

```

Graph showing the predicted values of VWC from the quadratic model graphed against the actual VWC. Notably, the zig-zag pattern improves slightly in the temperature-compensated model, but it is far from eliminated.

```{r 'Soil_predict_comparison', echo = F}

# Plot all the EMU probes vs actual VWC
cal %>%
    
    # Filter for after 7/22, when probes hit a minimum
    filter(date >= as.POSIXct("2017-07-22 00:00")) %>%
    
    # Gather all the probes together
    gather(probe, value, gold_vwc, gold_vwc_temp, silver_vwc) %>%
    
    arrange(desc(probe)) %>%

    # Make the plot
    ggplot(aes(x = vwc, y = value, color = probe)) +
    
        # Add a line with a slope of 1 and intercept of 0
        geom_abline(intercept = 0, slope = 1) + 
    
        # Add points
        geom_point() +
    
        # Set up the colors and legend
        scale_color_manual(values = c("gold", "darkgoldenrod", "gray60"), 
            name = "Probe", labels = c("Gold", "Gold Temp", "Silver")) +
    
        # Add axis labels
        xlab(bquote(bold('Actual VWC'~(m^3/m^3)))) +
        ylab(bquote(bold('Predicted Probe VWC'~(m^3/m^3)))) + 

        # Add theme
        ggplot.theme + 
    
        # Change legend position
        theme(legend.position = c(0.14, 0.85))

```

### Session Information

```{r 'Session_Info', echo = F, comment = ""}

# Add session information to help with reproduceability
sessionInfo()

```

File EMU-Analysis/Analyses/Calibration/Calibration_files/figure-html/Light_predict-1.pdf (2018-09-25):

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
- ●●
- ● ●

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
●●●●

- ●
- ●

●

●
●● ●

●

- ●
- ●●●
●●
●● ●●

●
0

500

1000

1500

2000

0 | 500 | 1000 | 1500 | 2000

# LiCor PFD (µmol m⁻² s⁻¹ )

# Predicted Sensor PFD (µmol

m

−

2

s

−1 )

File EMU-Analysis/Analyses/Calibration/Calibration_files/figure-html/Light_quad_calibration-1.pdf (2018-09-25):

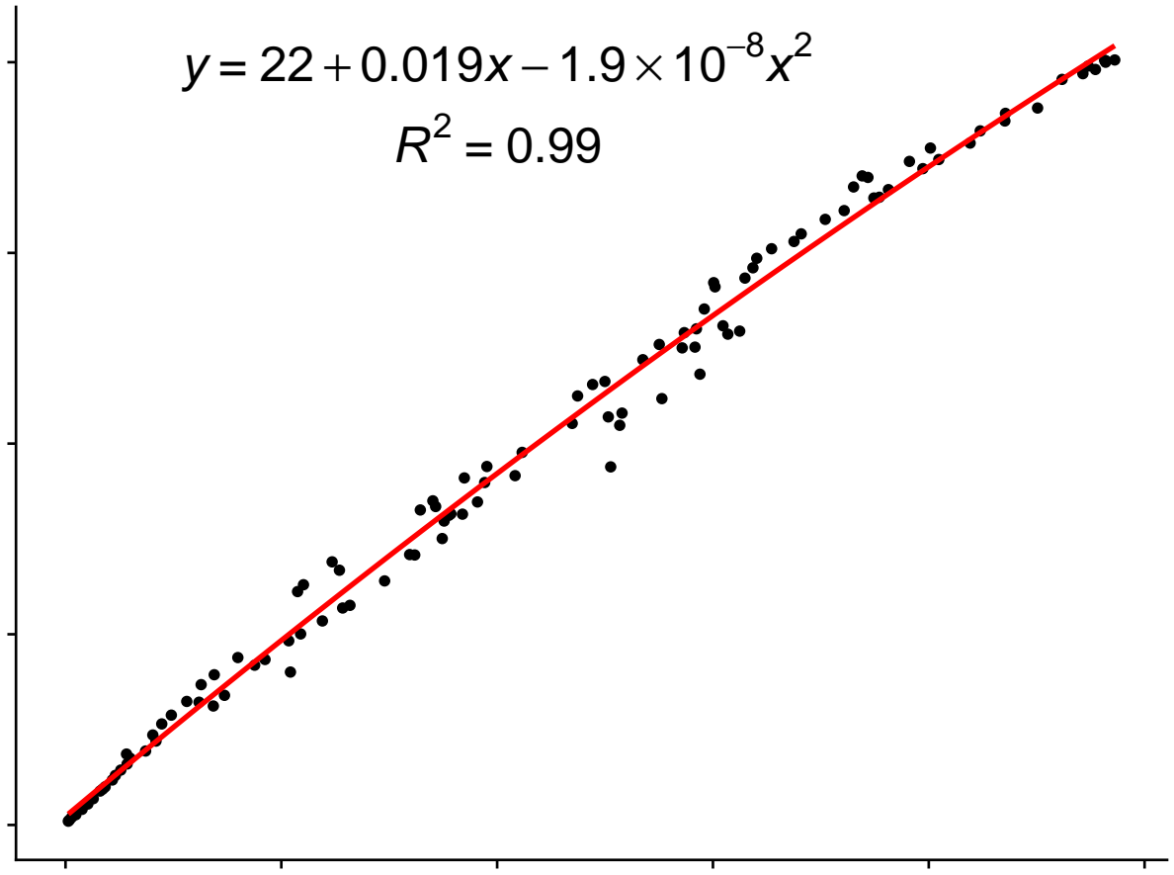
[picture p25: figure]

0

500

1000

1500

2000

0 | 25000 | 50000 | 75000 | 100000 | 125000

# Sensor Value (Lux)

# LiCor PFD (µmol

m

−

2

s

−1 )

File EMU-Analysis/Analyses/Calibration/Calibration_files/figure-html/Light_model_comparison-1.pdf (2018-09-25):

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
- ●●
- ● ●

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
●●●●

- ●
- ●

●

- ●● ●

●

- ●

●● ●● ●●
●● ●●

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
- ●●
- ● ●

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
●●●●

- ●
- ●

●

●
●● ●

●

- ●
- ●●●
●●
●● ●●

●
0

500

1000

1500

2000

0 | 500 | 1000 | 1500 | 2000

# LiCor PFD (µmol m⁻² s⁻¹ )

# Calibrated PFD (µmol

m

−

2

s

−1 )

# Model

●

●

# Linear Quadratic

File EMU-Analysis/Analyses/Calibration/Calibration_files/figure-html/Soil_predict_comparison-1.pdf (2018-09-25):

●

- ●

●

●●●●●
●
●● ●●● ●●●● ●●●● ●●

●●

●●

●●●●
- ●●

●●●

●●●●●
●●

●

●●●●
●●●●●●●●●●●●●
●

●●●●●● ●●●●● ●●●● ●●●● ●
●● ● ●●●●

●●

●●

●●
●●●●

●●

●●●●●

●●●
●●●●
●●●
●●

●●

●
●● ● ●
●●● ●●●● ● ●● ●●●●●● ●●●●●● ●●● ●

●

- ●

●
●●●●●●●●●

●●●●●● ●●●●●●●●
●●●

●●●
●●●●
●●●

●●●●●●●●●
●●● ●●●●●

●● ●●●● ●●

●●●
●● ●●●●●●
●●●●●

●●●●●●●●●●●●●●
●●●●●●●●●●
●●●●
●●

●●●●●●●●●●
●●●●●●

●●●●●●●●●●●● ●●●●●●●●●●●●

●●●●●●●●●●●●● ●

●●●
●
●
●●●●
●

●●●
●●● ●●●●●●●●●

●●●●

●●●

●●●●●
●

●●

●●●●
●●●
●●
●●●●●
●●●●●●●●● ●●●●

●●● ●
●● ●

●●●●●● ● ●

●●●●
●●●●

●●● ●●●●●● ●●●●

●●●●
●●

●●
●●●

●●●● ●●●●●●●●●●

●●●●●

●●●●●●●●●●●
●●●●●●●

●●
●●●●●● ●●●●
●●●

●
●●●●●
●●

●
●

●●●●●●

●

●

●●●● ●

●●●●●●● ●●●●● ●●

●●●

●●●
●●

●●● ●●●●●●
●●●●●
●●●●●●●●●●●●●●●

●

●●●●●
●●●● ●●● ● ●
- ● ●●●

●

●●

●●●● ●

●●●●
●●
●●●
●●
●●
●●

●
- ●● ●
●●●
●●● ●● ●●●●

●●● ●●● ●●●●●●

0.1

0.2

0.3

0.1 | 0.2 | 0.3

# Actual VWC (m³ m³

)

# Predicted Probe VWC

(

m

3

m

3

)

# Probe

●

●

●

# Gold Gold Temp Silver

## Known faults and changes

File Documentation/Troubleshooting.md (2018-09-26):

# Troubleshooting

Through experience, we have found that the complicated nature of EMU circuitry and frequent use of students without prior electronics experience often leads to problems.  Nearly all of these are apparent before deploying in the field, even with multiple testing. We find that the best defense is frequent quality checks at each step: this is often more efficient than troubleshooting, which is not always trivial. A wire plugged in the wrong address can produce complex symptoms, and is not easy to spot.

The following are common problems we have encountered, and some suggestions on how to fix them. We provide a [sensor-tester.lua](/Useful%20Scripts/Testers/sensor-tester.lua) script, that can run a number of checks on a completed EMU.  Additionally, there are individual [tester scripts](/Useful%20Scripts/Testers/) for each of the sensors.

We also recommend running a completed EMU in the lab, or even ourdoors for up a few days to a week before deploying in the field.

## Problems Identified by [sensor-tester.lua](/Useful%20Scripts/Testers/sensor-tester.lua)

- **D1 Mini resets while running sensor-tester**
  - Suspect a sensor wiring problem shorting out one of the sensors
    - Remove all sensors, and plug in one at a time.  
    - Check that the wiring colors are as they should be
  - A sensor may also be defective
- **BME280**
  - BME280: FAIL - No sensor detected
    - Check the wiring to the BME280, and to the clock and other sensors (shared wiring)
    - The BME280 may be defective
  - BME280: FAIL - Sensor detected, some measurements invalid
    - The BME280 may be defective
    - Humidity measurements (and temperature to a lesser extent) sometimes fail when the sensor is wet.
  - BME280: FAIL - BMP280 detected instead
    - The BME280 module you are using has the wrong chip installed.  The BMP280 chip (which is rectangular, not square) does not include humidity measurements, but is otherwise the same.
- **BH1750**
  - BH1750: FAIL - Lua Module not present
    - Upload and compile the lua module
  - BH1750: FAIL - No Sensor Found
    - Check the wiring to the BH1750, and to the clock and other sensors (shared wiring)
    - The BH1750 may be defective
  - BH1750: FAIL - Lux out of Range
    - Unless the sensor is in very bright light, the sensor is defective, it is returning the max reading.
- **DS3231**
  - DS3231: FAIL - Lua Module not present
    - Upload and compile the lua module
  - DS3231: FAIL - No Clock Detected
    - Check the wiring to the clock, and to the sensors (shared wiring)
    - The clock may be defective
  - DS3231: FAIL - Time Not Set
    - Set the time on the clock
    - Check to make sure the clock is maintaining time after setting it
    - Check the clock battery
- **ADS1115**
  - ADS1115: FAIL - No Sensor Found
    - Check the wiring to the ADS1115, and to the clock and other sensors (shared wiring)
    - The ADS1115 may be defective
  - ADS1115: Ch0 FAIL - Measurement low:
    - The soil moisture probe module may not be connected to the breadboard/ADS1115
      - This results in readings in the 5000 range
      - Connect the wiring to the soil moisture module
    - The breadboard connections or wiring may be loose
      - This results in readings in the 20000-24000 range
      - Rewire or replace the breadboard
      - Make sure the voltage to the soil moisture module is ~3.3v
  - ADS1115: Ch0 FAIL - Measurement high:
    - Usually this is caused by supplying the wrong voltage to the soil moisture module
      - It should get 3.3v from F21, not the battery voltage of 5-6v

## Errors and Warnings in the EMU's Logfile

- **Code errors:** An unforseen error in the code was caught
  - Often these are coding/syntax errors
  - main() function failed, sleeping
    - The error is in the main function
  - startup() function failed, sleeping
    - The error is in the startup function
- **Module loading errors:** various effects.  
  - Make sure the module is saved and compiled on the D1 Mini. Sometimes they can get corrupted, so re-save.
  - Loading logging module failed, sleeping
    - This error cannot be saved to the logfile and is only printed out on the terminal
    - It puts the D1 Mini to sleep without measuring
  - Loading ds3231 module failed, sleeping
    - It puts the D1 Mini to sleep without measuring
  - Loading csv module failed
    - Measurements are taken, but the data will not be logged
  - Loading bh1750 module failed
    - Measurements will not be taken for the BH1750 sensor
  - Loading ads1115 module failed
    - Measurements will not be taken for the soil moisture sensor
- **Clock errors:** All of these will result in no measurement, and the D1 Mini will go to sleep rather than turn off
  - No DS3231 clock found
    - Defective clock or improper wiring
    - Check the clock wiring for incorrect or loose connections
  - Clock time not set
    - Set the clock time
    - Check that the clock isn't faulty.  Does it keep time and maintain time via battery when power is off?
    - Check that the clock battery is not dead
- **Sensor errors and warnings**
  - No BME280 sensor found
    - Defective BME280 sensor, or wiring problems
  - No BH1750 sensor found
    - Defective BH1750 sensor, or wiring problems
  - No ADS1115 ADC found
    - Defective ADS1115 module, or plugged in the breadboard at the wrong place
  - Some measurements nil for BME280
    - A BME280 sensor is detected, but did not return values for some or all variables
    - Note: this can happen temporarily when the sensor is wet, especially for humidity readings
  - No measurement for BH1750
    - A BH1750 sensor is detected, but cannot be read. Likely that the sensor is defective, but could also be wiring.
  - BH1750 lux measurement out of range
    - A BH1750 sensor is detected and returned a value, but the value is the max 121556 lux. Unless in very bright sunlight, this indicates a defective sensor.
  - No soil moisture measurement from ADS1115
    - The ADS1115 is detected, but did not return a measurement. Likely a defective module, but could also be wiring between the soil moisture probe module and the ADS1115

## Miscellaneous Problems

- **Connecting to USB immediately shuts down computer, or computer warns about USB port power draw**
  - There is a short circuit somewhere on the breadboard or the D1 Mini itself: (+) and (-) are connected
- **Code starts running and then the D1 Mini resets without finishing the logging**
  - There is a short circuit somewhere, likely with the wires to one of the sensors or the clock
    - Generally, the reset/panic happens when trying to read the sensors
    - One of the sensors may be wired or plugged in incorrectly
- **Nothing turns on when the battery pack is switched on**
  - Check the voltage and switch of the battery pack
    - Voltage should be at least 3.5-4v (4xAA with new batteries should be 6.4v)
    - Switch should turn power on and off
  - Did the box recently log?  Wait until the next 15-minute interval
    - The clock alarm may be armed, turning off the power
    - If this is the case, you can trigger a logging event manually: connect A15 to ground to turn on the MOSFET.
  - Make sure the alarm wire from the clock is plugged into the breadboard at the MOSFET (E15-E18)
  - Check to make sure that the clock's time is set correctly
    - Make sure that it is not off by more than a few seconds
- **Blue LED on D1 Mini flashes rapidly**
  - This is usually an improper grounding/power problem, that can be difficult to fix
    - If you eavesdrop with a usb-to-serial connection without applying power, you'll see a bunch of debug/reset garbage come over the terminal
      - For example, using the CP2102 module mentioned in the parts list
      - Connect ground to ground, TX to RX, and RX to TX.
  - Inspect the ground wires plugged into A2, A11, and C2-C11
  - Inspect the soldering of the ground pin on the D1 Mini
  - Run a dupont wire between the ground rail on the 5V side and the ground pin at the top of the D1 Mini
  - Make sure the voltage of the battery pack is > 4V and ideally > 4.3-4.4v
  - As a last ditch effort, use a different breadboard
  - Another possible problem would be a coding error causing an immediate reset (usually in init.lua)
    - Try eavesdropping with a usb-to-serial connection to diagnose
    - Delete init.lua and save the file to the D1 Mini again, or reflash the firmware
- **After logging measurements, nothing turns off**
  - Check to make sure pin D5 is not connected to ground, which stops code from running
  - Check to make sure there is a 100k pullup resistor between D5 and 3.3V breadboard rail
  - Make sure you're on battery power and not on USB power.  The D1 Mini won't turn off on USB power
  - If the blue light on the D1 Mini flashes sporadically, the D1 Mini is resetting
    - This could be because of code errors or possibly sensor problems/corrosion
  - Several types of errors will cause the D1 Mini to go to sleep, but not the sensors.  Clock and soil moisture LEDs will stay on.
    - Problems with the clock
    - Errors in the lua code or the logfile module
  - You can use a usb-to-serial chip to eavesdrop on the D1 Mini while on battery power
    - Connect ground to ground, TX to RX, and RX to TX.  
    - Don't connect voltage from the usb to serial
- **D1 Mini runs and logs but does not wake up at the next 15-minute interval**
  - Make sure the clock and clock battery are not defective
  - Make sure the clock's time is set and it is maintaining time
  - Inspect and test the clock wiring
  - Make sure the single wire from the clock is plugged into the breadboard in the proper place in front of the MOSFET
  - Check the log file for any errors and make sure it is actually running correctly.  
- **LEDs on clock/soil moisture board glow weakly and don't turn off when on battery power**
  - The clock module has not been prepared properly.  Remove the middle 4.7k resistor block
- **Filesystem problems**
  - These may manifest as panics/crashes when loading the csv or logging modules.
  - Or problems reading or writing to files
  - Or troubles downloading Filesystem
  - Try re-uploading the csv and logging modules and starting fresh with the csv and log files (delete old ones)
  - Sometimes the only way to fix it is to re-flash the firmware and re-upload the software

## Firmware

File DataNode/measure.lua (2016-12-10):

--[[ 

This script reads the BME280, BH1750, and Soil Moisture sensors
It saves the data to CSV.
Built specifically for field usage

Module requirements:
ads1115, bh1750, csv, ds3231, logging


Firmware Module requirements:
bit, bme280, file, gpio, i2c, node, rtctime, sntp, tmr, u8g, wifi

##### Version History #####
- 10/13/2016 JGM - Version 0.1:
        - Initial version
        
- 11/22/2016 JGM - Version 1.0:
        - Version for Tim to take to South AFrica
        
- 11/28/2016 JGM - Version 1.1:
    - Now uses dynamic timers for all timer-related stuff.  
      This avoids conflicts, but requires a recent firmware

- 12/1/2016  JGM - Version 1.2:
    - Code is much more memory efficient, and there is much 
      more built-in error checking using pcall() to catch errors
      and prevent panics. Problems with modules loading or not 
      connected should get caught.

--]]

-- ########## Setup Variables ##########

-- Keep all functions local to save memory
local round, digs, display, timestamp, main, startup

-- Use local variables to save memory
-- These variables are still available to functions, eg startup() & main()
local sda, scl, soilPin, soilDelay, bme, log, disp,
    lux, tempC, humid, kPa, soil, timestr, log, disp, disp_addr

-- Set the SDA and SCL pins to use for I?C communication
sda = 1 -- GPIO4
scl = 2 -- GPIO5

-- Set the pin to turn on the soil sensor
soilPin = 7

-- Set the delay before using the soil sensor
soilDelay = 500

--Set the display's I2C address
disp_addr = 0x3c

-- Make sure interval is set correctly, and set to 1 minute otherwise
interval = interval ~= nil and interval or 1

-- Make sure timezone is set and default to UTC-5
timezone = timezone ~= nil and timezone or -5


-- ########## Ancillary Functions ##########


-- Function to round floating point numbers
function round(number, digits)
    local mult = 10^(digits or 0)
    return math.floor(number * mult + 0.5) / mult
end


-- Function to display # of digits for date/time
function digs(number, digits)
    return string.format("%0" .. (digits or 0) .. "d", number)
end


-- Function to update the display
-- All the stuff to put on the display goes inside the repeat .. until loop
function display()

    -- Start at the first display page, and draw until the last page is reached
    disp:firstPage()
    repeat
    
        -- Display all our stuff
        disp:drawStr( 5, 10, "Soil Moist.: " .. soil)
        disp:drawStr( 5, 20, "Temp: " .. tempC)

        -- Make sure we have humidity
        if bme == 2 then disp:drawStr( 5, 30, "Humid: " .. humid) end
        disp:drawStr( 5, 40, "Light: " .. lux)
        disp:drawStr( 5, 50, "Pressure: " .. kPa)
        disp:drawStr( 5, 60, timestr)
        
    until disp:nextPage() == false      
  
end


-- Function to get a Unix timestamp, and if specified, sync time with rtctime module
function timestamp(year, month, day, hour, minute, second, sync)

    local seconds, leapdays
    
    -- Calculate leap days
    leapdays = math.floor((year + 28) / 4 + 1)

    -- Determine if this is a leap year, and account for whether the leap day has occurred
    if (year - 1972) % 4 == 0  and month <= 2 then leapdays = leapdays - 1 end

    -- Days already elapsed in previous month for each month of the year.  
    local months = {0, 31, 59, 90, 120, 151, 181, 212, 243, 273, 304, 334}

    -- Check for errors from an unconnected or unconfigured DS3231
    if month == nil or month == 165 then
        seconds = 0
    else
        -- Calculate seconds since Unix Epoch = Unix Timestamp
        seconds = (365 * 86400 * (year + 30)) + (months[month] * 86400) + 
            ((day + leapdays - 1) * 86400) + 
            (hour * 3600) + (minute * 60) + second
    end

    -- Sync with the RTC time module if sync is true
    if sync then rtctime.set(seconds) end

    -- Return the timestamp
    return seconds
end


-- ########## Startup Routine ##########


function startup()

    -- Local variables that aren't needed outside of startup()
    local status, second, minute, hour, date, month, year, time


    -- ########## Initialize the logging module  ##########


    -- Load the logging module
    status, log = pcall(require, "logging")

    -- Log an error and exit if the module didn't load
    if not status then print("Error: logging module failed to load. Exiting!"); return end
    
    -- Specify a filename, logging all messages
    log.init("logfile.txt")
    
    -- Only log errors
    --log.init("logfile.txt", 1)
    
    -- Log the start
    log.log("Starting up ...", 3)


    -- ########## Get the time and set a wake-up alarm ##########


    -- Load the ds3231 module, making sure it loads properly
    status, ds3231 = pcall(require, "ds3231")

    -- Log an error and exit if the module didn't load
    if not status then log.log("DS3231 module failed to load. Exiting!", 1); return end
    
    -- Initialize the DS3231 real time clock
    ds3231.init(sda, scl)
    
    -- Get date and time (don't need to get day of week, so skip that)
    second, minute, hour, _, date, month, year = ds3231.getTime()
    
    -- Make a Unix timestamp and sync with the rtctime module (needed for logging)
    time = timestamp(year, month, date, hour, minute, second, true)
    
    -- Check if we got a valid time and log a warning if not.  
    if time == 0 then log.log("DS3231 module failed to get time", 2) end
    
    -- Creat a formatted date/time string
    timestr = month .. "/" .. digs(date, 2) .. "/" .. digs(year, 2) .. 
        " " .. digs(hour, 2) .. ":" .. digs(minute, 2) .. ":" .. 
        digs(second, 2) .. " UTC" .. timezone
    
    -- Set the next alarm to wake up the ESP at
    -- This will wake up the ESP after the interval specified, on the minute
    ds3231.setAlarm(1, ds3231.MINUTE, 0, minute + interval)

    -- Unload the DS3231 real time clock module
    ds3231 = nil
    package.loaded.ds3231 = nil


    -- ########## Initialize soil moisture pin ##########
    
    
    -- Set the soil pin to output mode so it can send electricity
    gpio.mode(soilPin, gpio.OUTPUT)
    
    -- Set the soil pin to Low (Off)
    gpio.write(soilPin, gpio.LOW)

    
    -- ########## Initialize Temp/Humidity sensor ##########
    
    
    -- Initialize BME280 temp/humidity/pressure sensor in sleep mode (power efficiency)
    bme = bme280.init(sda, scl, nil, nil, nil, 0)
    
    -- Log message
    if bme == nil then
        log.log("No BME/BMP280 sensor found. Exiting!", 1)
        return
    elseif bme == 2 then
        log.log("BME280 sensor found", 3)
    else
        log.log("BMP280 sensor found", 3)
    end


    -- ########## Initialize the display ##########
    
    
    -- Initialize I2C communication with the display
    i2c.setup(0, sda, scl, i2c.SLOW)
    
    -- Start the display driver for this particular display
    disp = u8g.ssd1306_128x64_i2c(disp_addr)
    
    -- Set the display font to use
    -- Options: font_5x8, font_6x10, font_7x13, font_9x15_78_79, font_9x15, font_chikita
    disp:setFont(u8g.font_6x10)


    -- ########## Run the main code to measure ##########


    -- Finished starting up.  
    -- Exit the function first to free up memory by waiting to run main()
    tmr.create():alarm(10, tmr.ALARM_SINGLE, function()
    
        -- Run garbage collection to get back memory
        collectgarbage()

        -- run the main code to take a measurement
        main()
    end)

end


-- ########## Main Code ##########


-- The main() function measures all our sensors and writes to display & csv
function main()

    -- Local variables that aren't needed outside of main()
    local status, pressure, temp, humidity, data

    -- Log message
    log.log("Starting a measurement ...", 3)

    -- Turn on soil moisture sensors
    gpio.write(soilPin, gpio.HIGH)

    -- Load the BH1750 light module
    status, bh1750 = pcall(require, "bh1750")

    -- Log an error if the module fails to load
    if not status then log.log("BH1750 module did not load", 1); return end

    -- Initialize bh1750, high resolution, one time (goes to sleep afterwards)
    bh1750.init(sda, scl, 0x23, "OneTime_H")

    -- Set the measurement time to the minimum: 117,000 lux
    bh1750.setMeasurementTime(32)

    -- Start getting a lux measurement
    bh1750.getLux(function(lx)

        -- Log message
        if lx ~= nil then
            log.log("Got lux measurement: " .. lx, 3)
        else
            log.log("Error measuring lux. Exiting!", 1)
            return
        end

        -- Save the value
        lux = round(lx, 2)

        -- Done with bh1750, so we can unload it 
        bh1750 = nil
        package.loaded.bh1750 = nil

    end)
    

    -- Take readings from BME280 in forced mode, and then go back to sleep
    -- The callback function runs after 113ms by default (or set first arg to # of ms)
    -- This gives time for the sensor to take the readings
    bme280.startreadout(0, function ()

        -- Get pressure & temperature from BME280
        pressure, temp = bme280.baro() -- hectopascals * 1000, tempC * 100

        -- Get humidity from BME280, if BMP280 don't bother
        if bme == 2 then humidity = bme280.humi() end -- RH * 1000

        -- Log message
        if pressure ~= nil and temp ~= nil and (humidity ~= nil or bme == 1) then
            log.log("Got BMP/BME measurements successfully", 3)
        else
            log.log("Error getting measurements from BMP/BME. Exiting!", 1)
            return
        end
        
        -- Unit conversions
        tempC = temp / 100 -- To Celcius

        -- Check to see if humidity is defined first
        if humidity ~= nil then humid = humidity / 1000 end -- To relative humidity percentage
        kPa = pressure / 10000 -- hectopascals * 1000

        --tempF = tempC * 9 / 5 + 32 -- To Fahrenheit
        --inHG = kPa * 0.295301 -- To inches of mercury
        
        -- Barometric correction for inHG by temperature
        -- From http://www.csgnetwork.com/barcorrecttcalc.html
        --correction = inHG * ((tempF - 28.630) / (1.1123 * tempF + 10978))
        --inHG = round(inHG + correction, 3)

        

    end)

    -- Log message
    log.log("Soil moisture sensor equilibrating", 3)


    -- Set a timer to wait until the soil sensors equilibrate
    tmr.create():alarm(soilDelay, tmr.ALARM_SINGLE, function()

        -- Log message
        log.log("Soil moisture sensor ready", 3)

        -- Load ADS1115 module
        status, ads1115 = pcall(require, "ads1115")
    
        -- Log an error if the module fails to load
        if not status then log.log("ADS1115 module did not load.  Exiting!", 1); return end
        
        -- Initialize ADS1115 module, sets up configuration
        ads1115.init(sda, scl)
    
        -- Maximum voltage to measure is 4.096 volts
        ads1115.setPGA(4.096)
    
        -- Read channel A0 using callback function
        ads1115.readADC(0, function(return_val)
    
            -- Get the soil moisture value from the callback
            soil = return_val

            -- Log message
            if soil ~= nil  then
                log.log("Got soil moisture successfully: " .. soil, 3)
            else
                log.log("Error getting soil moisture from ADS1115.  Exiting!", 1)
                return
            end
    
            -- Done with ads1115, so we can unload it 
            ads1115 = nil
            package.loaded.ads1115 = nil

            -- Turn off soil moisture sensor
            gpio.write(soilPin, gpio.LOW)
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

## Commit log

2016-08-23 Added some information on firmware
    How to flash, and the current firmware information
2016-08-23 Added i2c scanner script
    This script is helpful in finding where i2c devices are connected and what their addresses are
2016-08-31 ADS1115 version 0.3
    * Deals with negative numbers correctly, including in single shot mode
    * Added mvolts() function to convert values into millivolts
    * Added setComparator() function to enable and configure the comparator
    * Added setMode() function to set single shot or continuous mode
    * Numerous bug fixes, and cleaned up code considerably
2016-09-02 readADC() can now use a callback function
    This eliminates the problem of using tmr.delay() improperly. Now, if an optional callback function is specified as the second argument, then it will run after conversion is finished (the delay). The 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
    Also fixed error in setRate() that led to improper delays.
2016-09-02 Rewrote comparator to use optional arguments
    Also changed the argument order
    No longer tests to see whether high > low. This is up to the user, and doesn’t seem to break anything.
2016-11-11 Added the measure script
    This is what we’re working off of for the current iteration of the sensor.
2017-02-23 Some improvements to the bh1750 module
    - Added an i2c_id variable to the ads1115 module
    - Added a check in the init function to detect whether a sensor was found
2017-03-25 Modules now print their version info when loaded
2017-05-10 config.lua no longer includes obsolete volt_adj parameter
2017-06-21 Added final EMU data from the Fenton Experiment
    [Charlotte-data.csv, Marie-data.csv, MaryLee-data.csv, Natalie-data.csv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]
2017-06-21 Added new EMU placement data for the reboot
    [emu-sitedata-v2.csv]
2017-06-21 Combined the iButton data and added times
    [ibuttons-combined.csv]
2017-06-21 Pendant Hobo data
    [FM1.csv, FM2.csv, FM3.csv, FM4.csv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]
2017-06-21 Improved the ibutton combined datafile
    [ibuttons-combined.csv]
2017-06-21 Fixed column name in hobo FW2 datafile
    [FW2.csv]
2017-06-21 Added hobos to the sitedata csv
    [emu-sitedata-v2.csv]
2017-06-22 Fixed fenton data problems
    [emu-sitedata-v2.csv]
2017-06-23 Fixed another error in the Fenton dataset
    [emu-sitedata-v2.csv]
2017-06-23 Added sensor comparison analysis @ Fenton
2017-06-23 Updated Sensor comparisons
2017-08-23 Beginnings of soil moisture calibration for the fenton meadow soil.
    [Fenton_soil_calibration.csv]
2017-09-26 Added LiCor calibration data for the light sensor using our calibration rig
    [licor-calibration.csv]
2017-09-26 Cleaned up calibration analyses for soil moisture and light sensors
2017-09-28 Added code to write out CSVs of the calibration coefficients for soil/light
2017-09-28 Fixed location of calibration coefficent files
    [light-calibration.csv]
2017-09-28 Updated Sensor Comparison analysis, cleaning up graphs
2017-09-28 Updated fenton data processor to use calibration for vwc and par, updated dataset.
2017-09-28 Added some description to the sensor comparison
2018-01-29 Latest version of sensor comparision analysis
2018-01-29 Fixed bug in bh1750 sensor
2018-04-09 Updated calibration code to include root mean square error measures
    [light-calibration.csv]
2018-04-30 Added between-transect coefficients
    [transect.coeff.csv]
2018-04-30 Replaced PAR with PFD in graphs
    [light-calibration.csv]
2018-05-16 Moved testers to different folder, updated main sensor tester
2018-05-16 Correct version of sensor-tester
2018-05-16 Fixed soil temp error in sensor tester
2018-09-25 Cleaned up calibration analysis for publication
    [Fenton_soil_calibration.csv, gold-soil-calibration.csv, silver-soil-calibration.csv]
2018-09-25 Cleaned up sensor comparison analysis for publication
2018-09-25 Updated transect comparison model coefficients
    [transect.coeff.csv]
2018-09-26 Added and cleaned up documentation
    [EMU v1 fritzing diagram.fzz]
2018-09-26 Added readme and example for bh1750 module. Fixed bug resulting in improper readings when sensor was not present
2018-09-28 Added section on sensor shielding
2018-09-28 rewrote sensor tester scripts
2018-11-29 fixed minor error in sensor-tester.lua
2018-11-29 Updated individual sensor testers for publication
